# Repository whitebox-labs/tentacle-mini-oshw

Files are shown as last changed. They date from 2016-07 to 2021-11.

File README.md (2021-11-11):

model `T2.16`

# Introduction

Tentacle Mini

## What's the Tentacle Mini?
An Arduino shield to host and individually isolate up to 2 sensor circuits from Atlas Scientific to measure PH, Dissolved Oxygen, Electric Conductivity (E.C.) and Oxidation-Reduction Potential (ORP), RTD (Temperature).

* 2 channels
* 3.3V and 5V compatible
* I2C only

Individually isolated measurement circuits and communication lines prevent noise and ground loops for precise measurements.

## Getting Started
* [Documentation Site](https://www.whiteboxes.ch/docs/tentacle/t2)
* [Quick Start Tutorial](https://www.whiteboxes.ch/docs/tentacle/t2/#/quickstart)
* [How to switch EZO Circuits to I2C](https://www.whiteboxes.ch/docs/tentacle/t2/#/protocols)

## Code Examples
* [Continuous Readings](https://www.whiteboxes.ch/docs/tentacle/t2/#/continuous-example)
* [Continuous, Asynchronous Readings](https://www.whiteboxes.ch/docs/tentacle/t2/#/asynchronous-example)
* [Interactive, Bidirectional Communications](https://www.whiteboxes.ch/docs/tentacle/t2/#/interactive-example)
* [Download all examples (zip)](https://github.com/whitebox-labs/tentacle-examples/archive/master.zip)
* [Examples repository on GitHub](https://github.com/whitebox-labs/tentacle-examples)
`git clone https://github.com/whitebox-labs/tentacle-examples.git`

## Downloads
* [Tentacle Setup Sketch](https://raw.githubusercontent.com/whitebox-labs/tentacle-examples/master/arduino/tentacle-setup/tentacle_setup/tentacle_setup.ino ':target=_blank')
* [T2.16 Mechanical Drawing (PDF)](https://github.com/whitebox-labs/tentacle-mini-oshw/raw/master/hardware/mechanical/tentacle_t2_mechanical.pdf)
* [BNC Connector Mechanical Drawing (PDF)](https://github.com/whitebox-labs/tentacle/raw/master/hardware/mechanical/bnc_mechanical.pdf)
* [T2.16 Schematic (PDF)](https://github.com/whitebox-labs/tentacle-mini-oshw/raw/master/hardware/T2_mini_schematic.pdf)
* [T2.16 3D-Model (STL)](https://github.com/whitebox-labs/tentacle-mini-oshw/raw/master/hardware/mechanical/tentacle_t2.STL) ([view online](https://github.com/whitebox-labs/tentacle-mini-oshw/blob/master/hardware/mechanical/tentacle_t2.STL))
* [T2.16 3D-Model (STEP)](https://github.com/whitebox-labs/tentacle-mini-oshw/raw/master/hardware/mechanical/tentacle_t2.STEP)

## Support
For customer support, please use the [contact form](https://www.whiteboxes.ch/contact/) on our website.

If you find bug in the documentation, examples or the schematic, feel free to create an issue or even a pull request here on GitHub.

## Open Source
The Tentacle Shield is [certified](http://certificate.oshwa.org/certification-directory/) Open Source Hardware with UID CH000002. Schematics and layout are licensed under [Creative Commons BY-SA 4.0](http://creativecommons.org/licenses/by-sa/4.0/). Silkscreen graphics and the trade mark “Tentacle” are intellectual property of Whitebox Labs

* [Hardware source files on GitHub](https://github.com/whitebox-labs/tentacle-mini-oshw) `git clone https://github.com/whitebox-labs/tentacle-mini-oswh.git`

Made with KiCAD logo (http://kicad.org/)

## Buy
* From [our store](https://www.whiteboxes.ch/shop/tentacle-mini/) – we ship worldwide
* or from one of our [Distributors](https://www.whiteboxes.ch/distributors)

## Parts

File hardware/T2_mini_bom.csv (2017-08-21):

Id | Description | Package | Qty | Designator | Designation
1 | 1x6-pin female header .1inch | .1 inch header | 1 | SHIELD1 | ARDUINO_SHIELD
2 | 1x8-pin female header .1inch | .1 inch header | 2 | SHIELD1 | ARDUINO_SHIELD
3 | 1x10-pin female header .1inch | .1 inch header | 1 | SHIELD1 | ARDUINO_SHIELD
4 | LDO voltage regulator | SOT89 | 2 | REG1,REG2 | LD2981ABU50TR
5 | Digital signal isolator | so-8 | 2 | SIG_ISO1, SIG_ISO2 | SI8600
6 | SMD resistor 4.7K, 1/8W | SM0805 | 6 | R5,R6,R4,R3,R2,R1 | 4.7K
7 | Multilayer Ceramic Capacitor 0.1uF | SM0805 | 4 | C9,C4,C10,C5 | 0.1 µF
8 | Multilayer Ceramic Capacitor 1uF | SM0805 | 4 | C2,C6,C1,C7 | 1µF
9 | Multilayer Ceramic Capacitor 2.2uF | SM0805 | 2 | C8,C3 | 2.2µF
10 | Tantalum Capacitor 470uF | c_tant_x | 1 | C11 | 470µF
11 | Tactile push button | B3S-1000P | 1 | SW1 | SW_PUSH
12 | Isolated DC/DC converter 5V | R1SE_0505 | 2 | DCDC1,DCDC2 | R1SE_0505
13 | BNC Connector | BNC-1337542 | 2 | P1,P2 | BNC
14 | 1x3-pin female header .1inch | 1x3 .1 inch spacing female pin | 4 | STP1,STP2 | ATLAS_STAMP

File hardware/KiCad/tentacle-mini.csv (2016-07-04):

Id | Designator | Package | Quantity | Designation | Supplier and ref
1 | SW1 | B3S-1000P | 1 | SW_PUSH
2 | fiducial,fiducial | fiducial | 2 | VAL**
3 | P2,P1 | BNC-1337543a | 2 | BNC
4 | REG2,REG1 | sot89a | 2 | LD2981ABU50TR
5 | SIG_ISO1,SIG_ISO2 | so-8a | 2 | SI8600
6 | C2,C6,C1,C7 | SM0805a | 4 | 1µF
7 | R5,R6,R4,R3,R2,R1 | SM0805a | 6 | 4.7K
8 | C8,C3 | SM0805a | 2 | 2.2µF
9 | C9,C4,C10,C5 | SM0805a | 4 | 0.1 µF
10 | DCDC2,DCDC1 | R1SE_0505 | 2 | R1SE_0505
11 | C11 | c_tant_X | 1 | 470µF
12 | SHIELD1 | ARDUINO_SHIELD_040pinsb_no_outline | 1 | ARDUINO_SHIELD
13 | STP1,STP2 | Atlas_Stamp_14x21 | 2 | ATLAS_STAMP
14 | VAL,VAL | blackbox | 2 | REF
15 | VAL | mini_F.SilkS_68.5mm | 1 | REF
16 | VAL | mini_B.SilkS_68.5mm_flipped | 1 | REF
17 | VAL | icon | 1 | REF

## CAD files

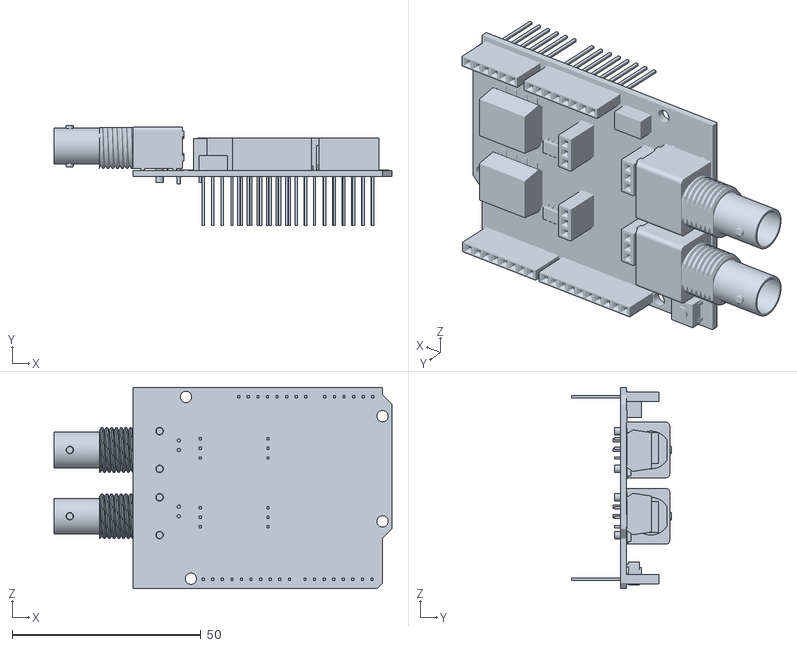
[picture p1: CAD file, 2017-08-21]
hardware/mechanical/tentacle_t2.STL
89.6 x 26.6 x 53.3

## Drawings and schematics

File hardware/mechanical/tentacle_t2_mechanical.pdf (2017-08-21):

14 2.50

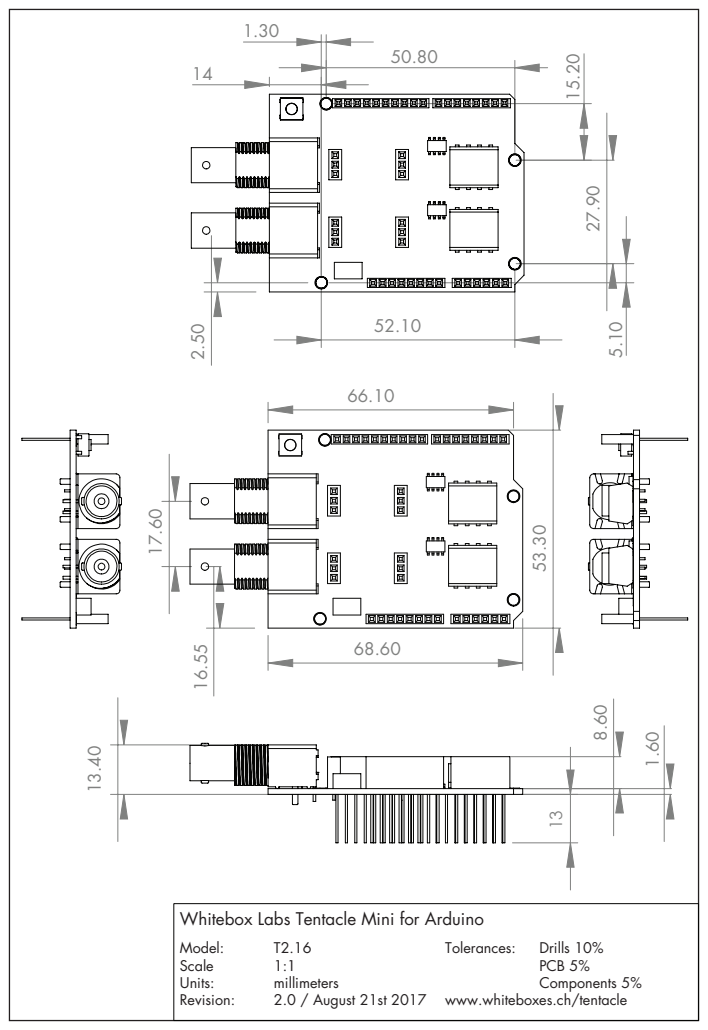
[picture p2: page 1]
Tolerances:; Drills 10%; PCB 5% Components 5%; Model:; Scale; Units:; millimeters; Revision:; 2.0 / August 21st 2017

Whitebox Labs Tentacle Mini for Arduino

www.whiteboxes.ch/tentacle

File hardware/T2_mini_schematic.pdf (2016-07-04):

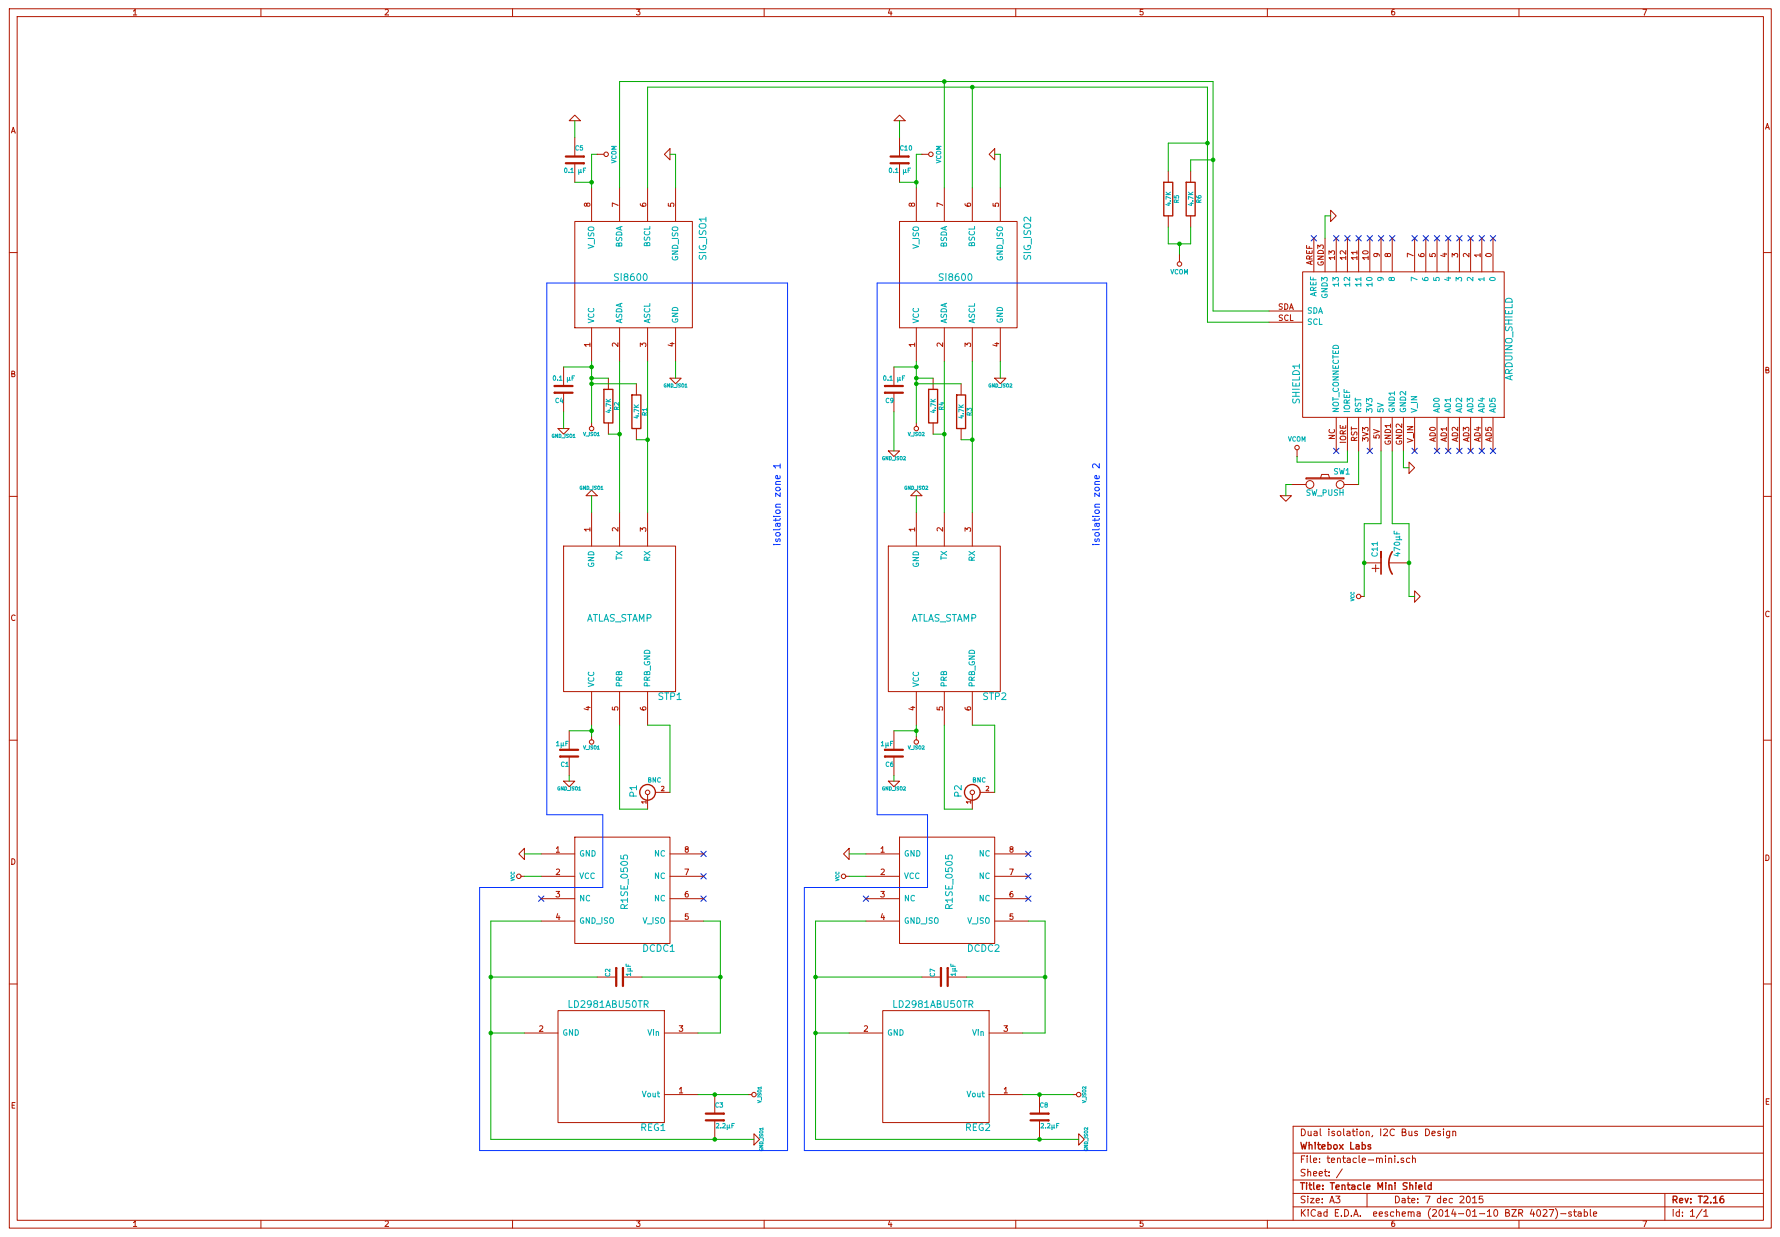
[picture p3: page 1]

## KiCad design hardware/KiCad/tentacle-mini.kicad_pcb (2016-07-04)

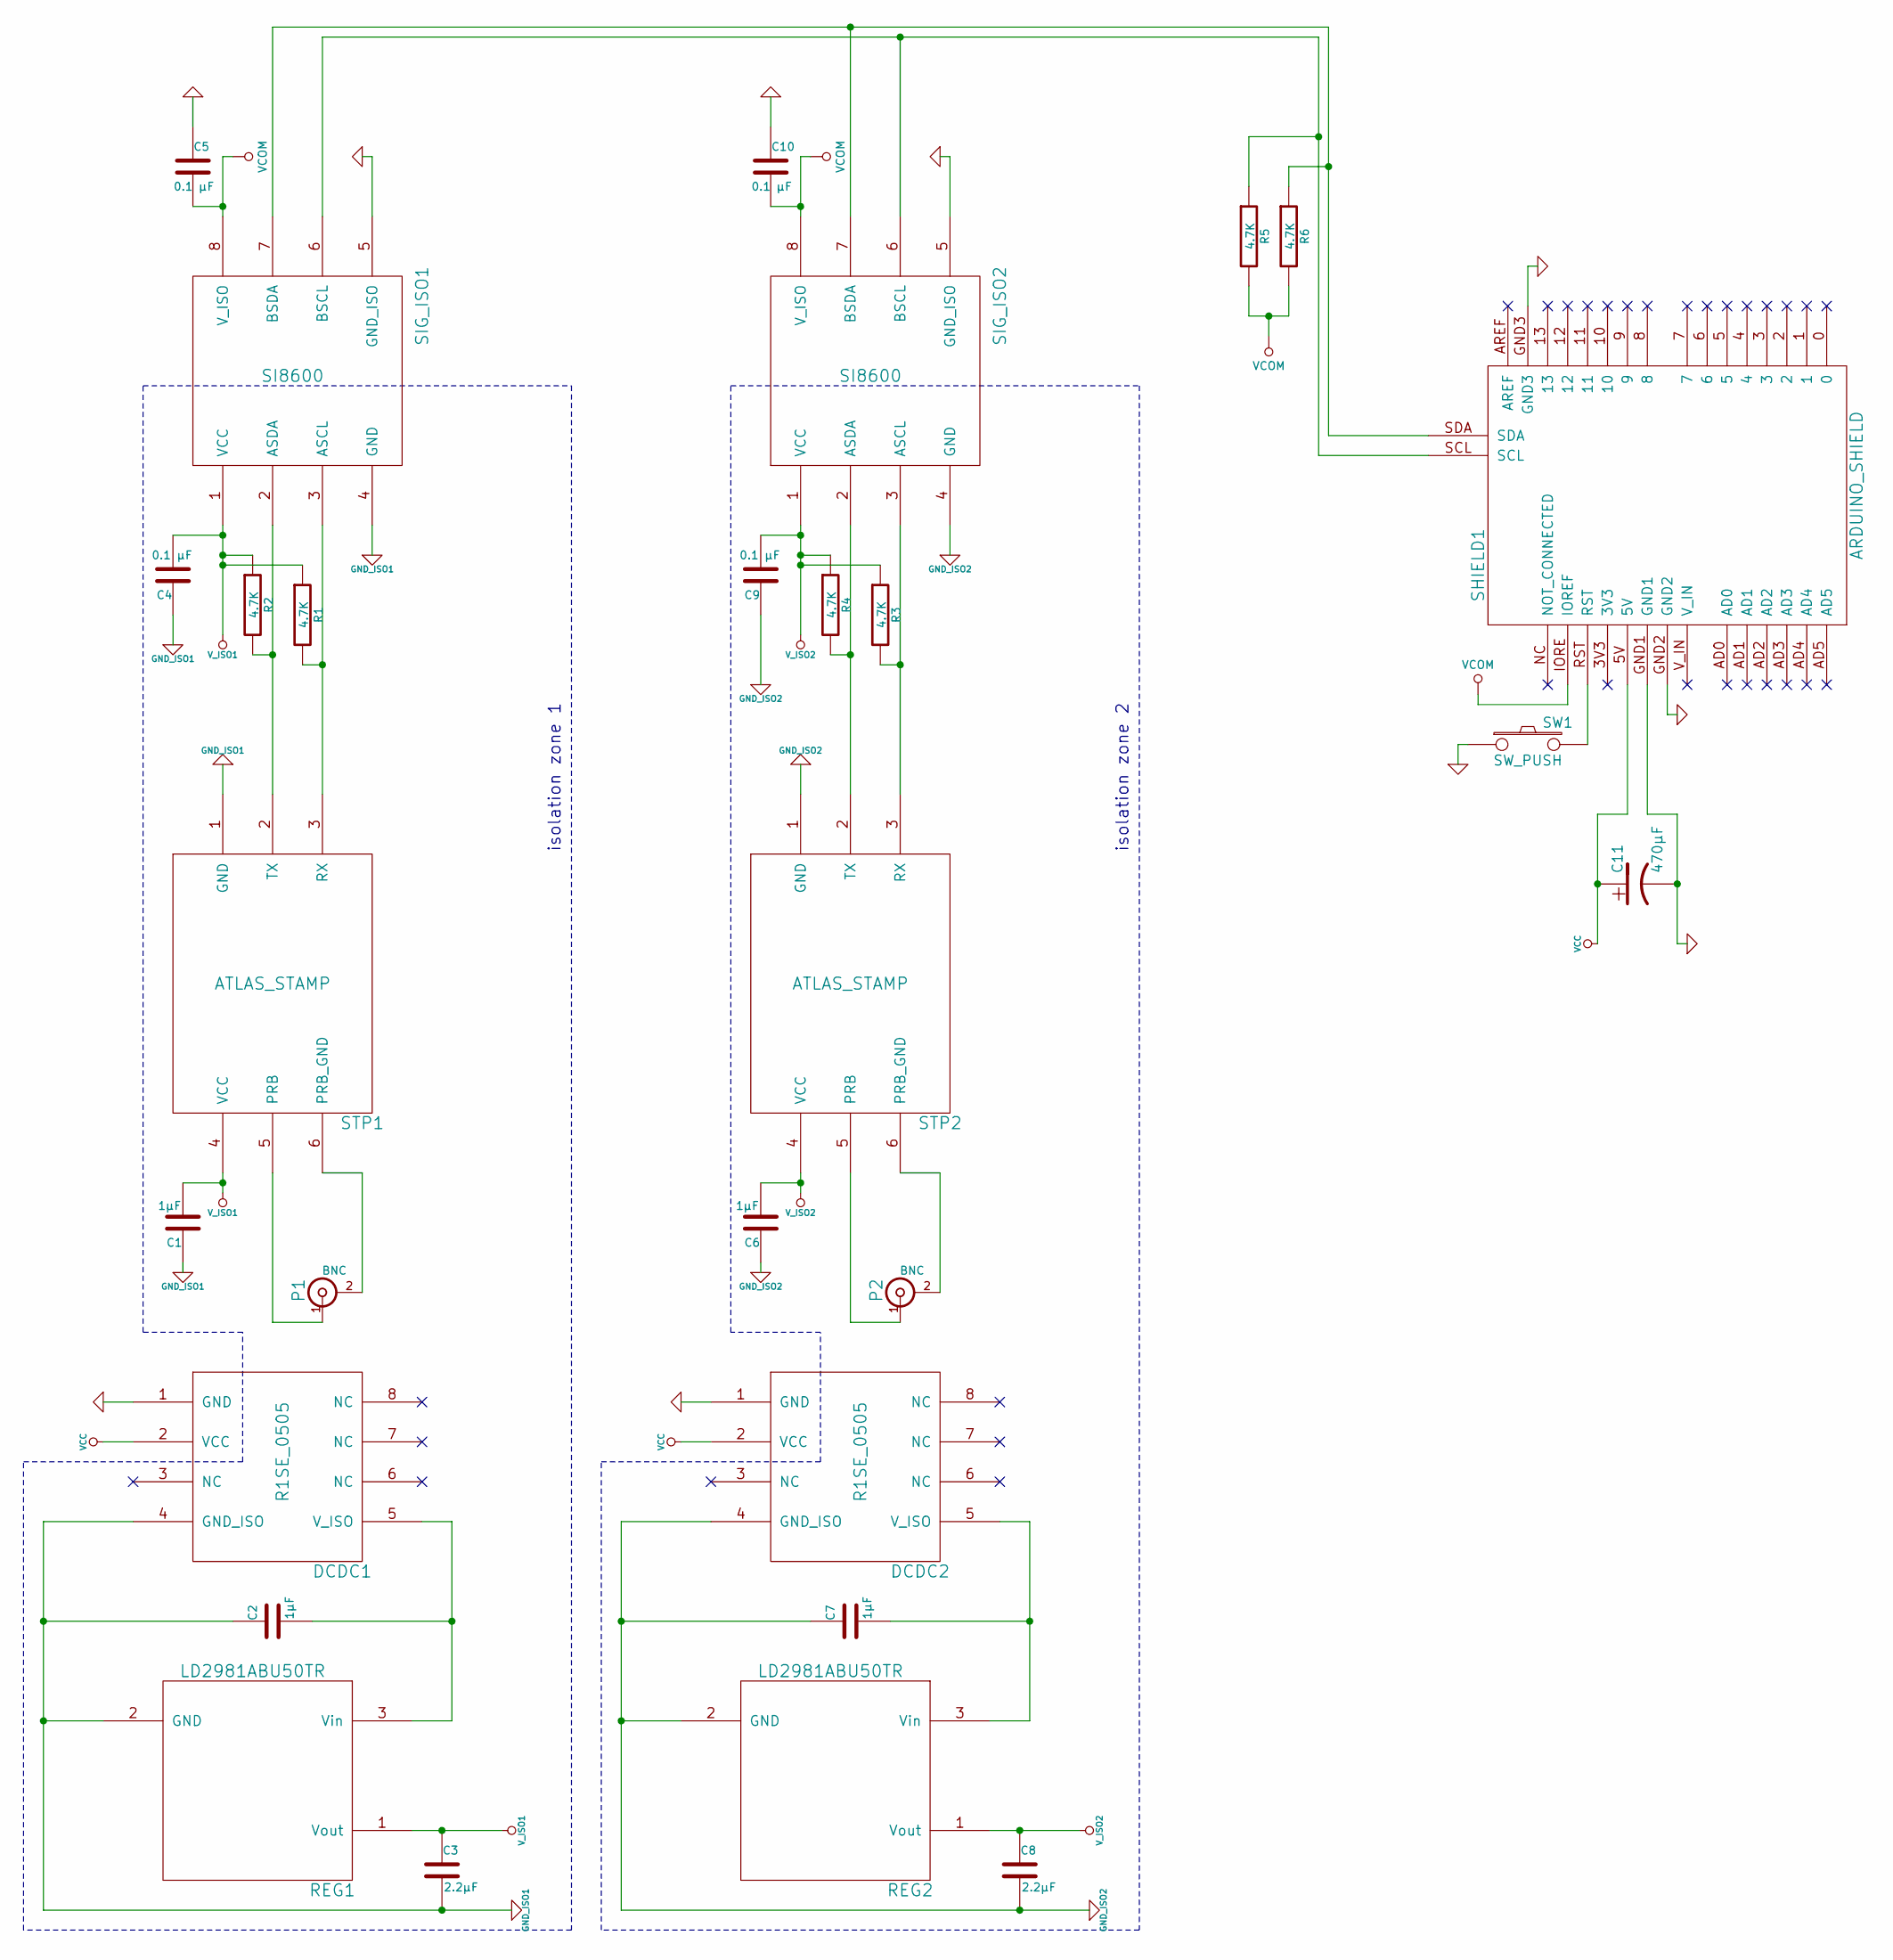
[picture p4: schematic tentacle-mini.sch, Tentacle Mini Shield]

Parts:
C1, C2, C6, C7: 1µF
C3, C8: 2.2µF
C4, C5, C9, C10: 0.1 µF
C11: 470µF
DCDC1, DCDC2: R1SE_0505
P1, P2: BNC
R1, R2, R3, R4, R5, R6: 4.7K
REG1, REG2: LD2981ABU50TR
SHIELD1: ARDUINO_SHIELD
SIG_ISO1, SIG_ISO2: SI8600
STP1, STP2: ATLAS_STAMP
SW1: SW_PUSH

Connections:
GND: C5.1, C10.1, C11.2, DCDC1.1 (GND), DCDC2.1 (GND), SHIELD1.GND1, SHIELD1.GND2, SHIELD1.GND3, SIG_ISO1.5 (GND_ISO), SIG_ISO2.5 (GND_ISO), SW1.1
GND_ISO1: C1.1, C2.1, C3.2, C4.1, DCDC1.4 (GND_ISO), REG1.2 (GND), SIG_ISO1.4 (GND), STP1.1 (GND)
GND_ISO2: C6.1, C7.1, C8.2, C9.1, DCDC2.4 (GND_ISO), REG2.2 (GND), SIG_ISO2.4 (GND), STP2.1 (GND)
unnamed: SHIELD1.RST, SW1.2
unnamed: C2.2, DCDC1.5 (V_ISO), REG1.3 (Vin)
unnamed: C7.2, DCDC2.5 (V_ISO), REG2.3 (Vin)
unnamed: R2.2, SIG_ISO1.2 (ASDA), STP1.2 (TX)
unnamed: R6.1, SHIELD1.SDA, SIG_ISO1.7 (BSDA), SIG_ISO2.7 (BSDA)
unnamed: R4.2, SIG_ISO2.2 (ASDA), STP2.2 (TX)
unnamed: R3.2, SIG_ISO2.3 (ASCL), STP2.3 (RX)
unnamed: R1.2, SIG_ISO1.3 (ASCL), STP1.3 (RX)
unnamed: R5.1, SHIELD1.SCL, SIG_ISO1.6 (BSCL), SIG_ISO2.6 (BSCL)
unnamed: P1.2 (Ext), STP1.6 (PRB_GND)
unnamed: P1.1 (In), STP1.5 (PRB)
unnamed: P2.2 (Ext), STP2.6 (PRB_GND)
unnamed: P2.1 (In), STP2.5 (PRB)
VCC: C11.1, DCDC1.2 (VCC), DCDC2.2 (VCC), SHIELD1.5V
VCOM: C5.2, C10.2, R5.2, R6.2, SHIELD1.IORE (IOREF), SIG_ISO1.8 (V_ISO), SIG_ISO2.8 (V_ISO)
V_ISO1: C1.2, C3.1, C4.2, R1.1, R2.1, REG1.1 (Vout), SIG_ISO1.1 (VCC), STP1.4 (VCC)
V_ISO2: C6.2, C8.1, C9.2, R3.1, R4.1, REG2.1 (Vout), SIG_ISO2.1 (VCC), STP2.4 (VCC)

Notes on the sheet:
isolation zone 1
isolation zone 2

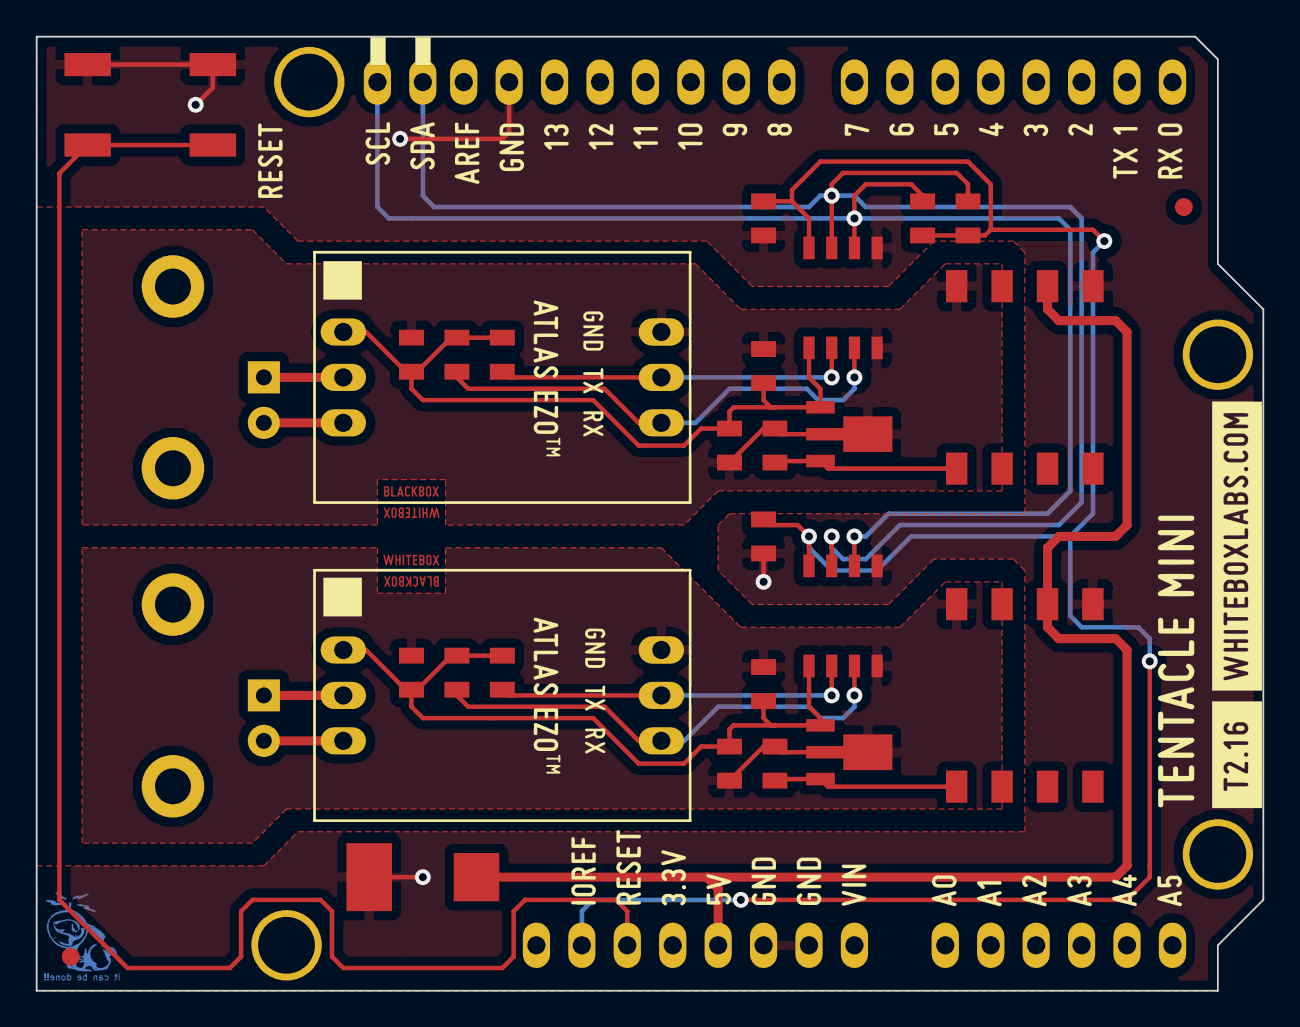
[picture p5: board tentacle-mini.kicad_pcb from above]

Board: 2 copper layers, 68.6 x 53.3 mm, 36 parts (0 on the bottom side), 20 nets.

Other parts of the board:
VAL: REF; mini_F.SilkS_68.5mm
VAL#2: REF; icon
VAL#3: REF; mini_B.SilkS_68.5mm_flipped
VAL#4, VAL#5: REF; blackbox
fiducial: VAL**; fiducial
fiducial#2: VAL**; fiducial

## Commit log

2016-07-04 Initial public commit
    [tentacle-mini-B_Cu.gbl, tentacle-mini-B_Mask.gbs, tentacle-mini-B_SilkS.gbo, tentacle-mini-Edge_Cuts.gbr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]
2016-07-04 added bom and pdf schematics
    [T2_mini_bom.csv]
2017-08-21 bom updated
    [T2_mini_bom.csv]
2017-08-21 csv error fixed
    [T2_mini_bom.csv]
2017-08-21 removed silkscreen gerbers
    [tentacle-mini-B_SilkS.gbo, tentacle-mini-F_SilkS.gto]
2017-08-21 added detailed 2d-drawing and 3d model
    [tentacle_t2.STL]
2018-08-25 added STEP 3D model
    [tentacle_t2.STEP]
2018-09-21 zipped STEP model for easier download
    [tentacle_t2.STEP]
2021-11-10 Update README.md
    https://forum.kicad.info/t/warning-avoid-all-links-to-kicad-pcb-org-use-kicad-org/31521
